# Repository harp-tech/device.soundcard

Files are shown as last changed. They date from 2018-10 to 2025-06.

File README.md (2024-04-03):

## Harp Soundcard
This is a high performance sound card with two output channels using 24 bits DACs at 192kHz sample rate. 

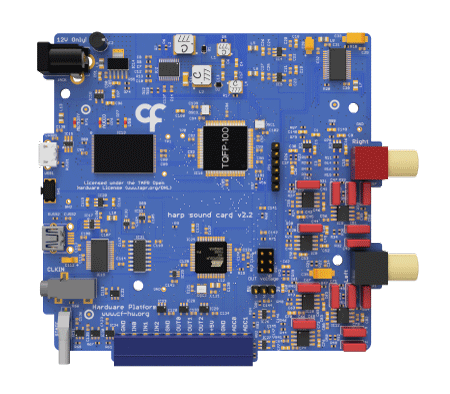
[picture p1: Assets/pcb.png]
HarpSoundcard


### Hardware Compatibility

| HW Version | Board                    | Board HW Version  | Notes                             |
| ---------- | ------------------------ |------------------ | --------------------------------- |
| **All**    | [Peripheral.AudioAmp][1] | >= 2.0            |                                   |

[1]: https://github.com/harp-tech/peripheral.audioamp

### Firmware Compatibility

| FW Version | Board                 | Board HW Version | Notes                                   |
| ---------- | --------------------- | ---------------- | --------------------------------------- |
| **>= 2.2** | [Device.SoundCard][2] | >= 1.0           | Bpod serial communication not supported |
| **<= 2.2** | [Device.SoundCard][2] | >= 1.0           |                                         |

[2]: https://github.com/harp-tech/device.soundcard

### Key Features ###

* Internal memory to store sounds, enabling low-latency sound delivery
* Pre-selected sounds can be triggered using an external TTL
* Internal wave generator allows the user to configure a pure tone without loading a sound file
* Stereo 24 bit @ 192 kHz maximum sampling rate outputs
* THD: -111dB (1 kHz @ 2 V rms)
* Noise Floor:	20 µV rms | -94 dB (20 Hz – 80 kHz)
* SNR:	100 dB | 113 dbA (20 Hz – 80 kHz @ 2 V rms)

### Connectivity ###

* 1x clock sync input (CLKIN) [stereo jack]
* 1x USB (for computer communication) [USB Mini-B]
* 1x micro USB (for sounds loading) [USB Micro-B]
* 1x 12V supply [barrel connector jack]
* 1x reset button [tactile switch]
* 1x output for the left channel [RCA]
* 1x output for the right channel [RCA]
* 3x general purpose digital outputs (3.3V or 5V) (OUT0-OUT2) [screw terminal]
* 3x general purpose digital inputs (5V tolerant) (IN0-IN2) [screw terminal]
* 2x analog inputs (3.3V máx - 5V tolerant) (ADC0-ADC1) [screw terminal]

## Interface ##

The interface with the Harp Soundcard can be done through [Bonsai](https://bonsai-rx.org/) or a dedicated GUI (Graphical User Interface).

### Install Graphical User Interface (GUI) ###

In order to use this GUI, there are some software that needs to be installed:

1 - Install the [drivers](https://bitbucket.org/fchampalimaud/downloads/downloads/UsbDriver-2.12.26.zip).

2 - Install the [runtime](https://bitbucket.org/fchampalimaud/downloads/downloads/Runtime-1.0.zip).

3 - Reboot the computer.

4 - Install the [GUI](https://bitbucket.org/fchampalimaud/downloads/downloads/Harp%20Sound%20Card%20v1.2.1.zip).

### Install Drivers ###

To install the proper drivers to interface with the device, follow the next steps in sequence.

1 - Connect both Harp Sound Card's USB ports to the computer.

2 - Launch the previously installed Harp Sound Card GUI.

3 - Click on the button Open Drivers folder and launch the zadig-2.3.exe.

4 - (1) Select the Harp Sound Card from the list. If the device is not available, go to Options -> List All Devices.

5 - (2) Select the WinUSB driver and click Install WCID Driver.

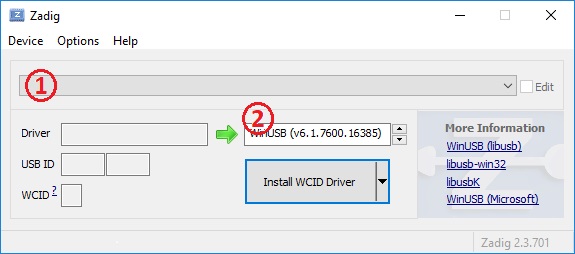
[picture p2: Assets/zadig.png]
Zadig


## Firmware ##

### Tagging Scheme ###

|Tag|Description|
|-|-|
|SoundCard-*|Firmware for the sound card's microcontroller (8 bits processor)|
|SoundCard.PIC32-*|Firmware for the sound card's 32 bits processor|

### Firmware Update ###

1 - Install the [Harp Converto to CSV](https://bitbucket.org/fchampalimaud/downloads/downloads/Harp_Convert_To_CSV_v1.8.3.zip).

2 - Open the Harp Convert to CSV application and write *bootloader* under List box on the Options tab

3 - Select the correspondent COM port and then select the firmware to be loaded for both microcontrollers 

# Licensing #

Each subdirectory will contain a license or, possibly, a set of licenses if it involves both hardware and software.

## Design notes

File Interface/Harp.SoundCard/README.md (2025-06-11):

## About

`Harp.SoundCard` provides an asynchronous API and reactive operators for data acquisition and control of [Harp SoundCard](https://harp-tech.org/api/Harp.SoundCard.html) devices.

## How to Use

To use `Harp.SoundCard` for visual reactive programming, please install this package using the [Bonsai package manager](https://bonsai-rx.org/docs/articles/packages.html).

The package can also be used from any .NET application:
```c#
using Harp.SoundCard;

using var device = await Device.CreateAsync("COM3");
var whoAmI = await device.ReadWhoAmIAsync();
var deviceName = await device.ReadDeviceNameAsync();
var timestamp = await device.ReadTimestampSecondsAsync();
Console.WriteLine($"{deviceName} WhoAmI: {whoAmI} Timestamp (s): {timestamp}");
```

## Additional Documentation

For additional documentation and examples, refer to the [official Harp documentation](https://harp-tech.org/api/Harp.SoundCard.html).

## Feedback & Contributing

`Harp.SoundCard` is released as open-source under the [MIT license](https://licenses.nuget.org/MIT). Bug reports and contributions are welcome at [the GitHub repository](https://github.com/harp-tech/device.soundcard).

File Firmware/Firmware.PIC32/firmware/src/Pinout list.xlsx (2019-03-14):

 | 0 | 1 | 2 | 3 | 4 | 5 | 6 | 7 | 8 | 9 | 10 | 11 | 12 | 13 | 14 | 15 |  | Pins | Description | Notes
RA | X | X | X | X | X | X | X | X |  | X | X |  |  |  | X | X |  | RB8 | !SS1
RB | X | X | X | X | X | X | X | X | X | X | X | X | X | X | X | X |  | RB9 | SDO1
RC |  | X | X | X | X |  |  |  |  |  |  |  | X | X | X | X |  | RB10 | SCK1
RD | X | X | X | X | X | X |  |  |  | X | X | X | X | X | X | X |  | RF0 | USB
RE | X | X | X | X | X | X | X | X | X | X |  |  |  |  |  |  |  | RF1 | AUDIO
RF | X | X | X | X | X | X |  |  | X |  |  |  | X | X |  |  |  | RG12 | TP0
RG | X | X |  |  |  |  | X | X | X | X |  |  | X | X | X | X |  | RG13 | TP1
 |  |  |  |  |  |  |  |  |  |  |  |  |  |  |  |  |  | RG14 | MEMORY
 |  |  |  |  |  |  |  |  |  |  |  |  |  |  |  |  |  | RD1 | EN_P12V
 |  |  |  |  |  |  |  |  |  |  |  |  |  |  |  |  |  | RD2 | EN_N12V
 |  |  |  |  |  |  |  |  |  |  |  |  |  |  |  |  |  | RB6-7 | ICE/ICD
 |  |  |  |  |  |  |  |  |  |  |  |  |  |  |  |  |  | RE0-7 | Memory | RE0 -> PMD0
 |  |  |  |  |  |  |  |  |  |  |  |  |  |  |  |  |  | RE8-9 | Don't use -- facilitates memory's access code
 |  |  |  |  |  |  |  |  |  |  |  |  |  |  |  |  |  | RC13 | REFCLKO1 (MCLK out) | I2S
 |  |  |  |  |  |  |  |  |  |  |  |  |  |  |  |  |  | RC14 | REFCLKI1 (OSC 24.576 MHz) (MCLK in) | I2S
 |  |  |  |  |  |  |  |  |  |  |  |  |  |  |  |  |  | RD9 | SS4 (out) (LRCLK) | I2S
 |  |  |  |  |  |  |  |  |  |  |  |  |  |  |  |  |  | RD10 | SCK4 (BCLK) | I2S
 |  |  |  |  |  |  |  |  |  |  |  |  |  |  |  |  |  | RD11 | SDO4 (SDATA) | I2S
 |  |  |  |  |  |  |  |  |  |  |  |  |  |  |  |  |  | RF2 | MUTE | Pin don't change
 |  |  |  |  |  |  |  |  |  |  |  |  |  |  |  |  |  | RF8 | ZEROR (not used)
 |  |  |  |  |  |  |  |  |  |  |  |  |  |  |  |  |  | RF3 | ZEROL (not used)
 |  |  |  |  |  |  |  |  |  |  |  |  |  |  |  |  |  | RF5 | DAC_RST | Pin don't change
 |  |  |  |  |  |  |  |  |  |  |  |  |  |  |  |  |  | RB12 (AN7) | ADC0_EZ
 |  |  |  |  |  |  |  |  |  |  |  |  |  |  |  |  |  | RB13 (AN8) | ADC1_EZ
 |  |  |  |  |  |  |  |  |  |  |  |  |  |  |  |  |  | RC3 | WE | Pin don't change
 |  |  |  |  |  |  |  |  |  |  |  |  |  |  |  |  |  | RC4 | RE | Pin don't change
 |  |  |  |  |  |  |  |  |  |  |  |  |  |  |  |  |  | RG7 | ALE | Pin don't change
 |  |  |  |  |  |  |  |  |  |  |  |  |  |  |  |  |  | RG8 | WP | Pin don't change
 |  |  |  |  |  |  |  |  |  |  |  |  |  |  |  |  |  | RG9 | BUSY | Pin don't change
 |  |  |  |  |  |  |  |  |  |  |  |  |  |  |  |  |  | RD12 | CE
 |  |  |  |  |  |  |  |  |  |  |  |  |  |  |  |  |  | RD13 | CLE
 |  |  |  |  |  |  |  |  |  |  |  |  |  |  |  |  | CMD_DATA | RA0-7 | PAR0-7: AVR <-> PIC32 Parallel bus with the Harp uController | (RA0 -> PAR0) Used to send configuration commands * | 2e-05
 |  |  |  |  |  |  |  |  |  |  |  |  |  |  |  |  |  | RA9-10, RA14-15 | Don't use -- facilitates parallel bus' code
 |  |  |  |  |  |  |  |  |  |  |  |  |  |  |  |  | CMD_WRITE | RB5 (INT3) | UC_IO0: AVR -> PIC32 | Command available on the PAR bus
 |  |  |  |  |  |  |  |  |  |  |  |  |  |  |  |  | CMD_LATCHED | RB4 | UC_IO1: AVR <- PIC32 | Command read from the PAR bus
 |  |  |  |  |  |  |  |  |  |  |  |  |  |  |  |  | SOUND_IS _ON | RG6 (INT2 if needed) | UC_IO2: AVR <- PIC32 | Command received has na error (must be set before CMD_LATCHED)
 |  |  |  |  |  |  |  |  |  |  |  |  |  |  |  |  | BOOTLOADER_EN | RB1 (INT4) | UC_IO3: AVR -> PIC32 | Enables bootloader on PIC32
 |  |  |  |  |  |  |  |  |  |  |  |  |  |  |  |  | CMD_NOT_EXEC | RB2 (INT1 if needed) | UC_IO4: AVR <- PIC32 | PIC32 has started (left bootloader or just boot)
 |  |  |  |  |  |  |  |  |  |  |  |  |  |  |  |  |  | RD0 (INT0) | IN0/TRIG: AVR & PIC32
 |  |  |  |  |  |  |  |  |  |  |  |  |  |  |  |  |  | IN01 | AVR
 |  |  |  |  |  |  |  |  |  |  |  |  |  |  |  |  |  | IN02 | AVR
 |  |  |  |  |  |  |  |  |  |  |  |  |  |  |  |  |  | RB3 | OUT00/SYNC: AVR & PIC32
 |  |  |  |  |  |  |  |  |  |  |  |  |  |  |  |  |  | OUT01 | AVR | 3.125e-08
 |  |  |  |  |  |  |  |  |  |  |  |  |  |  |  |  |  | OUT02 | AVR | 3.2e-05
 |  |  |  |  |  |  |  |  |  |  |  |  |  |  |  |  |  |  |  | 31250
 |  |  |  |  |  |  |  |  |  |  |  |  |  |  |  |  |  | RC2 (U2TX) | UART2_RX: AVR <- PIC32 (USED FOR PIC32 BOOLOADER) | Not used
 |  |  |  |  |  |  |  |  |  |  |  |  |  |  |  |  |  | RB0 (U2RX) | UART2_TX: AVR -> PIC32 (USED FOR PIC32 BOOLOADER) | Notifications
 |  |  |  |  |  |  |  |  |  |  |  |  |  |  |  |  | Plays a sound | 'P' n | d80
 |  |  |  |  |  |  |  |  |  |  |  |  |  |  |  |  | Stop all playback | 'X' | d88
 |  |  |  |  |  |  |  |  |  |  |  |  |  |  |  |  | Stop specific sound | x' n | d120

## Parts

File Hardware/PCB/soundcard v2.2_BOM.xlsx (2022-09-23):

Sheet: BOM
Part(s) | Quantity | Description | Distributor | Part. No.
IC1 | 1 | IC REG LINEAR 200MA TSOT23-5 | Digikey | ADP7118AUJZ-R7CT-ND
IC2 | 1 | IC REG BST SEPIC INV ADJ 20TSSOP | Mouser | 584-ADP5070AREZ
IC3 | 1 | IC REG LINEAR 200MA 5TSOT | Digikey | ADP7182AUJZ-R7CT-ND
IC4, IC5 | 2 | IC REG LINEAR 5V 150MA SOT23-5 | Digikey | LP2985A-50DBVT
IC6 | 1 | IC DAC AUDIO MULTIBIT 28-SSOP | Digikey | AD1955ARSZ-ND
IC7, IC8, IC9, IC10, IC11, IC12 | 6 | Amplificadores de precisão High Prec Low Noise Oper Amplifier | Mouser | 595-OPA228UA/2K5
IC13 | 1 | IC FLASH 2GBIT 48TSOP | Digikey | 1274-1040-ND‎
IC14 | 1 | Reguladores de tensão de LDO DMOS 1A LDO Reg | Mouser | 595-TPS73801DCQR
IC15, IC17 | 2 | TVS DIODE 5.25VWM 17VC SOT23-6 | Mouser | 511-USBLC6-2SC6
IC16 | 1 | IC MCU 32BIT 1MB FLASH 100TQFP | Mouser | 579-MZ1024EFM100IPF
IC19 | 1 | IC USB FS SERIAL UART 28-SSOP | Digikey | 768-1007-1-ND
IC18, IC20 | 2 | IC REG LINEAR 3.3V 250MA SOT23 | Digikey | 296-38557-1-ND
IC21 | 1 | DGTL ISO 3.75KV GEN PURP 16SOIC | Digikey | 336-2092-5-ND
IC22, IC24, IC30, IC31 | 4 | IC BUS BUFF TRI-ST N-INV SOT23-5 | Digikey | 296-11603-1-ND
IC23, IC28, IC29 | 3 | IC BUFF CMOS LVL/SFTR N-I 5TSOP | Digikey | M74VHC1GT50DTT1GOSCT-ND
IC25 | 1 | IC MCU 8BIT 128KB FLASH 44TQFP | Mouser | 556-ATXMEGA128A4U-AU
IC33, IC34 | 2 | IC BUFFER NON-INVERT 5.5V SC88A OE | Mouser | 863-M74VHC1GT126DF2G
IC35 | 1 | IC BUFFER NON-INVERT 5.5V SC88A !OE | Mouser | 863-M74VHC1GT125DF2G
R17 | 1 | RES SMD 5.36Ω 1% 0402 | Digikey | 541-5.36LLCT-ND
R5 | 1 | RES SMD 6.04Ω 1% 0402 | Digikey | 541-6.04LLCT-ND
R57 | 1 | RES SMD 1kΩ 1% 0402 | Digikey | P1.00KLCT-ND
R18, R75, R76, R77 | 4 | RES SMD 2.49kΩ 1% 0402 | Digikey | P2.49KLCT-ND
R10, R22 | 2 | RES SMD 2.8kΩ 1% 0402 | Digikey | P2.80KLCT-ND
R55, R80 | 2 | RES SMD 3.16kΩ 1% 0402 | Digikey | P3.16KLCT-ND
R7 | 1 | RES SMD 3.57kΩ 1% 0402 | Digikey | P3.57KLCT-ND
R13 | 1 | RES SMD 5.76kΩ 1% 0402 | Digikey | P5.76KLCT-ND
R8 | 1 | RES SMD 8.45kΩ 1% 0402 | Digikey | P8.45KLCT-ND
R74 | 1 | RES SMD 9.76kΩ 1% 0402 | Digikey | P9.76KLCT-ND
R3, R4, R15, R16, R56 | 5 | RES SMD 10kΩ 1% 0402 | Digikey | P10.0KLCT-ND
R12 | 1 | RES SMD 54.9kΩ 1% 0402 | Digikey | P54.9KLCT-ND
R6 | 1 | RES SMD 63.4kΩ 1% 0402 | Digikey | P63.4KLCT-ND
R9, R20, R61, R67, R68, R78, R79, R87, R88, R89 | 8 | RES SMD 100kΩ 5% 0402 | Digikey | P100KJCT-ND
R11 | 1 | RES SMD 150kΩ 1% 0402 | Digikey | P150KLCT-ND
R1, R2 | 2 | RES SMD 180kΩ 1% 0402 | Digikey | P180KLCT-ND
R14 | 1 | RES SMD 215kΩ 1% 0402 | Digikey | P215KLCT-ND
RUSB1, RUSB2 | 2 | RES SMD 1MΩ 5% 0402 | Digikey | P17211CT-ND
R27, R28, R37, R43, R44, R53, R66 | 7 | Resistores de Filme Fino - SMD 100Ω 0.5% 0402 25ppm | Mouser | 754-RG1005P-101DT10
R33, R34, R49, R50 | 4 | Resistores de Filme Fino - SMD 226Ω 0.1% 0402 25ppm | Mouser | 667-ERA-2AEB2260X
R35, R36, R51, R52 | 4 | Resistores de Filme Fino - SMD 324Ω 0.5% 0402 25ppm | Mouser | 754-RR0510P-3240D
R38, R54 | 2 | Resistores de Filme Fino - SMD 332Ω 0.5% 0402 25ppm | Mouser | 754-RG1005P-3320DT10
R31, R32, R47, R48 | 4 | Resistores de Filme Fino - SMD 681Ω 0.1% 0402 25ppm | Mouser | 667-ERA-2AEB6810X
R24, R25, R40, R41 | 4 | Resistores de Filme Fino - SMD 806Ω 0.5% 0402 25ppm | Mouser | 754-RG1005P-8060DT10
R23, R26, R29, R30, R39, R42, R45, R46 | 8 | Resistores de Filme Fino - SMD 2kΩ 0.1% 0402 25ppm | Mouser | 667-ERA-2AEB202X
R21 | 1 | Resistores de Filme Fino - SMD 2.21kΩ 0.5% 0402 25ppm | Mouser | 754-RR0510P-2211D
C8, C107, C108 | 3 | CAP SMD CER 47pF 50V ±5% C0G 0402 | Digikey | 490-8206-1-ND
C10 | 1 | CAP SMD CER 68pF 50V ±5% C0G 0402 | Digikey | 490-8219-1-ND‎
C38, C62 | 2 | CAP SMD CER 100pF 50V ±5% C0G 0603 | Digikey | 709-1147-1-ND
C7 | 1 | CAP SMD CER 820pF 50V ±5% C0G 0402 | Digikey | 445-8064-1-ND
CUSB1, CUSB2 | 2 | CAP SMD CER 4.7nF 50V ±10% X7R 0402 | Digikey | 490-4915-1-ND
C12 | 1 | CAP SMD CER 6.8nF 50V ±10% X7R 0402 | Digikey | 1276-1585-1-ND
C22, C23 | 2 | CAP SMD CER 10nF 50V ±10% X7R 0402 | Digikey | 490-4762-1-ND
C15, C20, C21, C24, C25, C29, C30, C31, C32, C84, C88, C89, C90, C92, C93, C94, C95, C96, C97, C98, C99, C101, C102, C104, C105, C106, C111, C113, C114, C117, C118, C119, C120, C121, C123, C126, C127, C128, C133, C134, C135, C136, C138, C139, C143 | 45 | CAP SMD CER 100nF 25V ±10% X5R 0402 | Digikey | 1276-1043-1-ND
C34, C37, C39, C40, C41, C42, C49, C50, C55, C56, C61, C63, C64, C65, C66, C73, C74, C79, C80 | 19 | CAP SMD CER 100nF 25V ±10% X5R 0402 | Digikey | 1276-1043-1-ND
C130, C131 | 2 | CAP SMD CER 330nF 10V ±10% X5R 0402 | Digikey | 1276-6665-1-ND
C3, C14, C137 | 3 | CAP SMD CER 1uF 25V ±10% X5R 0402 | Digikey | 1276-1445-1-ND
C4, C6, C13, C17, C148, C149 | 6 | CAP SMD CER 1uF 25V ±10% X5R 0603 | Digikey | 490-16608-1-ND
C1, C5, C9, C16 | 4 | CAP SMD CER 2.2uF 35V ±10% X5R 0603 | Digikey | 445-8025-1-ND
C112 | 1 | CAP SMD TAN 4.7uF 6.3V ±10% 1206 | Digikey | 399-9717-1-ND
C11 | 1 | CAP SMD CER 10uF 25V ±20% X5R 1206 | Digikey | 445-8806-1-ND
C18, C19, C26, C27, C85, C86, C87, C91, C100, C115, C116, C132 | 12 | CAP SMD CER 10uF 25V ±20% X5R 0603 | Digikey | 445-9015-1-ND
C28 | 1 | CAP SMD TAN 10uF 16V ±20% 1411 | Digikey | 399-8446-1-ND
C33, C35 | 2 | CAP SMD TAN 47uF 16V ±10% 2312 | Digikey | 399-9763-1-ND
C43, C44, C67, C68 | 4 | CAP TH FILM 100pF 100V ±5% PP Radial | Mouser | 505-FKP2100/100/5
C51, C54, C75, C78 | 4 | CAP TH FILM 2.7nF 100V ±2.5% PP Radial | Mouser | 505-FKP2D012701DHA00
C57, C81 | 2 | CAP TH FILM 3.9nF 63V ±5% PP Radial | Mouser | 505-FKP2-3900632.5A
C47, C48, C71, C72 | 4 | CAP TH FILM 5.6nF 63V ±5% PP Radial | Mouser | 505-FKP2C015601DHC00
C36, C45, C46, C52, C53, C58, C59, C60, C69, C70, C76, C77, C82, C83 | 14 | CAP SMD CER 4.7uF 25V ±20% X5R 0603 | Mouser | 81-GRM188R61E475ME1J
C2 | 1 | CAP TH ELEC 68uF 25V ±20% Alum Radial | Digikey | P14412-ND
L1, L4 | 2 | IND SMD 1.5uH 2.2A ±20% | Mouser | 994-LPS4012-152MRB
L2 | 1 | IND SMD 3.3uH 1.35A ±20% | Mouser | 994-LPS6225-332MRB
L3 | 1 | IND SMD 15uH 1.2A ±20% | Mouser | 994-LPS6225-153MRB
L5, L6, L7, L8, L9 | 5 | FERRITE BEAD 600Ω 500mA 300mΩ 0805 | Digikey | 240-2399-1-ND
L10, L12, L13 | 3 | FERRITE BEAD 70Ω 1.5A 50mΩ 0805 | Digikey | 240-2389-1-ND
D1, D2 | 2 | DIODE SCHOTTKY 30V 1A SOD323 | Digikey | BAS3010A03WE6327HTSA1CT-ND
STATE | 1 | LED GREEN 0603 SMD | Digikey | 751-1176-1-ND
MEMORY, AUDIO, USB | 3 | LED RED 0603 SMD | Digikey | 751-1182-1-ND
OSC1 | 1 | OSC MEMS 24.000MHZ CMOS | Mouser | ASEM1-24.000MHZ-LC-T
OSC2 | 1 | OSC MEMS 32.0000MHZ CMOS | Mouser | 579-SC1001CI50320000
OSC3 | 1 | OSC MEMS 24.576MHZ CMOS | Digikey | ASEMB-24.576MHZ-LY-T
USB2 | 1 | RECEPT MINI USB2.0 5POS | Digikey | H2960CT-ND
USB1 | 1 | CONN RCPT USB MICRO B SMD | Mouser | 798-ZX62D-B-5P830
CLKIN | 1 | JACK STEREO 3.5MM SMD R/A | Digikey | SC1489-1-ND
JP2 | 1 | CONN HEADER 3POS .100 STR | Digikey | 609-3470-ND
 | 1 | CONN JUMPER SHORTING GOLD FLASH | Digikey | S9001-ND
JP1 | 1 | CONN HEADER 6POS .100 STR | Digikey | 609-3256-ND
PDI | 1 | CONN HEADER 6POS .100 STR | Digikey | 609-3210-ND
J3 | 1 | CONN RCA JACK MONO 3.2MM R/A RED | Digikey | SC1853-ND
J4 | 1 | CONN RCA JACK MONO 3.2MM R/A BLACK | Digikey | SC1852-ND
JACK | 1 | CC PCB 2.1MM | Mouser | 163-179PH-EX
SW1 | 1 | SWITCH TACTILE SPST-NO 0.05A 50V | Digikey | 401-1097-1-ND
 | 1 | IMO 20.1550M/10-E Pluggable Terminal Block, 3.5 mm, 10 Ways | Farnell | 2575213
X1 | 1 | IMO 20.155MH/10-E Terminal Block, Header, 3.5 mm, 10 Ways | Farnell | 2575221
USB Cable Mini | 1 | USB A - MINI-B 1.5M - MINI-B 1.5M BLACK | Mouser | 538-88732-8702
USB Cable Micro | 1 | Cabo USB 2.0A to Micro B Cable 1M Blk Nylon | Mouser | 734-ES-UB1-100-BK
 | 3 | LIGHT PIPE ROUND 4MM CLEAR | Digikey | LPC_096_CTP-ND
 | 1 | Tubos de Luz LED CML LIGHTPIPE | Mouser | 606-7513D2-L
 | 1 | AC/DC Power Supply, Class II, 1 Output, 12 W, 12 V, 1 A | Farnell | 2524421
 | 1 | Heat Sink, Square, For PGA's, 18.6 °C/W, PGA, 14 mm, 14 mm, 14 mm | Farnell | 1850037
Components | 281
Licensed under the TAPR Open Hardware License (www.tapr.org/OHL)
Copyright 2021 Artur Silva, Filipe Carvalho

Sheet: Sheet1
r1 | 95300
r2 | 13300
11.46493395
5.273333333

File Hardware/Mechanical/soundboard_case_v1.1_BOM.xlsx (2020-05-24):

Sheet: BOM
Board | Part(s) | Quantity | Description | Distributor | Part. No. | Price/Unit | Total Price
 |  | 4 | Screw, Flat / Countersunk Head Pozidriv, M3, Nylon, 10 mm Length | Farnell | 1514427 | €0.14 | €0.55
 |  | 4 | Bumper / Feet, Recessed, Screw, Rubber, 6.4 mm, Round, Black | Farnell | 1651664 | €0.12 | €0.50
 |  | 4 | Standoff, Nylon 6.6 (Polyamide 6.6), M3, Hex Male-Female, 11 mm | Farnell | 2988203 | €0.91 | €3.64
 |  | 4 | Nut, Hex, M3, Nylon 6.6 | Farnell | 2472687 | €0.05 | €0.20
 | Components | 16 |  |  |  |  | €4.89
 | PCB
 | Assembly
 |  |  |  |  |  | Total | €4.89
 | Licensed under the TAPR Open Hardware License (www.tapr.org/OHL)
 | Copyright 2017-2019 Artur Silva, Dario Bento, Paulo Carriço and Filipe Carvalho

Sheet: Sheet1
r1 | 95300
r2 | 13300
11.46493395
5.273333333

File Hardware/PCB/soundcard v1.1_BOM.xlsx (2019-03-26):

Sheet: BOM
Board | Part(s) | Quantity | Description | Distributor | Part. No.
 | IC1 | 1 | IC REG LINEAR 200MA TSOT23-5 | Digikey | ADP7118AUJZ-R7CT-ND
 | IC2 | 1 | IC REG BST SEPIC INV ADJ 20TSSOP | Digikey | ADP5070AREZ-R7CT-ND
 | IC3 | 1 | IC REG LINEAR 200MA 5TSOT | Digikey | ADP7182AUJZ-R7CT-ND
 | IC4, IC5 | 2 | IC REG LINEAR 5V 200MA 8SOIC | Digikey | ADP3303ARZ-5-ND
 | IC6 | 1 | IC DAC AUDIO MULTIBIT 28-SSOP | Digikey | AD1955ARSZ-ND
 | IC7, IC8, IC9, IC10, IC11, IC12 | 6 | IC OPAMP GP 110MHZ 8SOIC | Digikey | AD797BRZ-ND
 | IC13 | 1 | IC FLASH 2GBIT 48TSOP | Digikey | 1274-1040-ND‎
 | IC14, IC32 | 2 | IC REG LIN POS ADJ 1A SOT223-6 | Digikey | 296-39489-1-ND
 | IC15, IC17 | 2 | TVS DIODE 5.25VWM 17VC SOT23-6 | Digikey | 497-5235-1-ND
 | IC16 | 1 | IC MCU 32BIT 2MB FLASH 100TQFP | Digikey | PIC32MZ2048EFM100-I/PF
 | IC19 | 1 | IC USB FS SERIAL UART 28-SSOP | Digikey | 768-1007-1-ND
 | IC18, IC20 | 2 | IC REG LINEAR 3.3V 250MA SOT23 | Digikey | 296-38557-1-ND
 | IC21 | 1 | DGTL ISO 3.75KV GEN PURP 16SOIC | Digikey | 336-2092-5-ND
 | IC22, IC24, IC30, IC31 | 4 | IC BUS BUFF TRI-ST N-INV SOT23-5 | Digikey | 296-11603-1-ND
 | IC23, IC28, IC29 | 3 | IC BUFF CMOS LVL/SFTR N-I 5TSOP | Digikey | M74VHC1GT50DTT1GOSCT-ND
 | IC25 | 1 | IC MCU 8BIT 128KB FLASH 44TQFP | Digikey | ATXMEGA128A4U-AU-ND
 | IC26 | 1 | DGTL ISO 2.5KV GEN PURP 16SOIC | Digikey | 336-2568-ND
 | IC27 | 1 | IC DVR/RCVR RS-485 3.3V 8-SOIC | Digikey | 296-19626-1-ND
 | IC33, IC34 | 2 | IC BUFFER NON-INVERT 5.5V SC88A OE | Digikey | M74VHC1GT126DF2GOSCT-ND
 | IC35 | 1 | IC BUFFER NON-INVERT 5.5V SC88A !OE | Digikey | M74VHC1GT125DF2GOSCT-ND
 | IC37, IC38 | 2 | Amplificadores operacionais - Amp Op 2.2V 50MHz Low Noise Single Supply | Mouser | 595-OPA365AIDBVR
 | R17 | 1 | RES SMD 5.36Ω 1% 0402 | Digikey | 541-5.36LLCT-ND
 | R5 | 1 | RES SMD 6.04Ω 1% 0402 | Digikey | 541-6.04LLCT-ND
 | R69, R70 | 2 | RES SMD 33Ω 1% 0402 | Digikey | P33.0LCT-ND
 | R66 | 1 | RES SMD 68Ω 1% 0402 | Digikey | P68.0LCT-ND
 | R57, R63 | 2 | RES SMD 1kΩ 1% 0402 | Digikey | P1.00KLCT-ND
 | R10 | 1 | RES SMD 2.8kΩ 1% 0402 | Digikey | P2.80KLCT-ND
 | R75, R76, R77 | 3 | RES SMD 2.05kΩ 1% 0402 | Digikey | P2.05KLCT-ND
 | R19, R55, R60, R62, R71, R72, R80 | 7 | RES SMD 3.16kΩ 1% 0402 | Digikey | P3.16KLCT-ND
 | R7 | 1 | RES SMD 3.57kΩ 1% 0402 | Digikey | P3.57KLCT-ND
 | R13 | 1 | RES SMD 5.76kΩ 1% 0402 | Digikey | P5.76KLCT-ND
 | R8 | 1 | RES SMD 8.45kΩ 1% 0402 | Digikey | P8.45KLCT-ND
 | R73, R74 | 2 | RES SMD 9.76kΩ 1% 0402 | Digikey | P9.76KLCT-ND
 | R3, R4, R15, R16, R56, R81, R82 | 7 | RES SMD 10kΩ 1% 0402 | Digikey | P10.0KLCT-ND
 | R84, R86 | 2 | RES SMD 16kΩ 1% 0402 | Digikey | P16.0KLCT-ND
 | R83, R85 | 2 | RES SMD 24kΩ 1% 0402 | Digikey | P24.0KLCT-ND
 | R12 | 1 | RES SMD 54.9kΩ 1% 0402 | Digikey | P54.9KLCT-ND
 | R6 | 1 | RES SMD 63.4kΩ 1% 0402 | Digikey | P63.4KLCT-ND
 | R9, R20, R61, R67, R68, R78, R79, R87, R88, R89 | 8 | RES SMD 100kΩ 5% 0402 | Digikey | P100KJCT-ND
 | R11 | 1 | RES SMD 150kΩ 1% 0402 | Digikey | P150KLCT-ND
 | R1, R2 | 2 | RES SMD 180kΩ 1% 0402 | Digikey | P180KLCT-ND
 | R14 | 1 | RES SMD 215kΩ 1% 0402 | Digikey | P215KLCT-ND
 | RUSB1, RUSB2 | 2 | RES SMD 1MΩ 5% 0402 | Digikey | P17211CT-ND
 | R27, R28, R37, R43, R44, R53 | 6 | RES TH 100Ω 1% Axial | Digikey | 100XBK-ND
 | R33, R34, R49, R50 | 4 | RES TH 226Ω 0.1% Axial | Mouser | 66-RC55LF-D-226
 | R35, R36, R51, R52 | 4 | RES TH 324Ω 1% Axial | Digikey | 324XBK-ND
 | R38, R54 | 2 | RES TH 332Ω 1% Axial | Digikey | 332XBK-ND
 | R31, R32, R47, R48 | 4 | RES TH 681Ω 0.1% Axial | Mouser | 66-RC55LF-D-681
 | R24, R25, R40, R41 | 4 | RES TH 806Ω 1% Axial | Digikey | 806XBK-ND
 | R23, R26, R29, R30, R39, R42, R45, R46 | 8 | RES TH 2kΩ 0.1% Axial | Mouser | 756-RC55Y-2K0BI
 | R21 | 1 | RES TH 2.21kΩ 1% Axial | Mouser | 2.21KXBK-ND
 | R18 | 1 | RES TH 2.49kΩ 1% Axial | Digikey | 2.49KXBK-ND
 | R22 | 1 | RES TH 2.80kΩ 1% Axial | Digikey | 2.80KXBK-ND
 | C8, C107, C108 | 3 | CAP SMD CER 47pF 50V ±5% C0G 0402 | Digikey | 490-8206-1-ND
 | C10 | 1 | CAP SMD CER 68pF 50V ±5% C0G 0402 | Digikey | 490-8219-1-ND‎
 | C38, C62 | 2 | CAP SMD CER 100pF 50V ±5% C0G 0603 | Digikey | 709-1147-1-ND
 | C7 | 1 | CAP SMD CER 820pF 50V ±5% C0G 0402 | Digikey | 445-8064-1-ND
 | CUSB1, CUSB2 | 2 | CAP SMD CER 4.7nF 50V ±10% X7R 0402 | Digikey | 490-4915-1-ND
 | C12 | 1 | CAP SMD CER 6.8nF 50V ±10% X7R 0402 | Digikey | 1276-1585-1-ND
 | C22, C23 | 2 | CAP SMD CER 10nF 50V ±10% X7R 0402 | Digikey | 490-4762-1-ND
 | C144, C145 | 2 | CAP SMD CER 15nF 16V ±10% X7R 0402 | Digikey | 1276-1524-1-ND
 | C15, C20, C21, C24, C25, C29, C30, C31, C32, C84, C88, C89, C90, C92, C93, C94, C95, C96, C97, C98, C99, C101, C102, C104, C105, C106, C109, C111, C113, C114, C117, C118, C119, C120, C121, C122, C123, C124, C125, C126, C127, C128, C129, C133, C134, C135, C136, C138, C139, C140, C141, C142, C143, C146, C147 | 55 | CAP SMD CER 100nF 25V ±10% X5R 0402 | Digikey | 1276-1043-1-ND
 | C130, C131 | 2 | CAP SMD CER 330nF 10V ±10% X5R 0402 | Digikey | 1276-6665-1-ND
 | C3, C14, C137 | 3 | CAP SMD CER 1uF 25V ±10% X5R 0402 | Digikey | 1276-1445-1-ND
 | C4, C6, C13, C17, C148, C149 | 6 | CAP SMD CER 1uF 25V ±10% X5R 0603 | Digikey | 490-16608-1-ND
 | C1, C5, C9, C16 | 4 | CAP SMD CER 2.2uF 35V ±10% X5R 0603 | Digikey | 445-8025-1-ND
 | C112 | 1 | CAP SMD TAN 4.7uF 6.3V ±10% 1206 | Digikey | 399-9717-1-ND
 | C11 | 1 | CAP SMD CER 10uF 25V ±20% X5R 1206 | Digikey | 445-8806-1-ND
 | C18, C19, C26, C27, C85, C86, C87, C91, C100, C103, C110, C115, C116, C132 | 14 | CAP SMD CER 10uF 25V ±20% X5R 0603 | Digikey | 445-9015-1-ND
 | C28 | 1 | CAP SMD TAN 10uF 16V ±20% 1411 | Digikey | 399-8446-1-ND
 | C33 | 1 | CAP SMD TAN 47uF 16V ±10% 2312 | Digikey | 399-9763-1-ND
 | C43, C44, C67, C68 | 4 | CAP TH FILM 100pF 100V ±5% PP Radial | Mouser | 505-FKP2100/100/5
 | C51, C54, C75, C78 | 4 | CAP TH FILM 2.7nF 100V ±2.5% PP Radial | Mouser | 505-FKP2D012701DHA00
 | C57, C81 | 2 | CAP TH FILM 3.9nF 63V ±5% PP Radial | Mouser | 505-FKP2-3900632.5A
 | C47, C48, C71, C72 | 4 | CAP TH FILM 5.6nF 63V ±5% PP Radial | Mouser | 505-FKP2C015601DHC00
 | C34, C37, C39, C40, C41, C42, C49, C50, C55, C56, C61, C63, C64, C65, C66, C73, C74, C79, C80 | 19 | CAP TH FILM 100nF 100V ±5% Poly Radial | Mouser | BFC237022104
 | C36, C45, C46, C52, C53, C58, C59, C60, C69, C70, C76, C77, C82, C83 | 14 | CAP TH ELEC 4.7uF 35V ±20% Alum Radial | Digikey | 493-1847-ND
 | C35 | 1 | CAP TH ELEC 47uF 16V ±20% Alum Radial | Digikey | P11196-ND
 | C2 | 1 | CAP TH ELEC 68uF 25V ±20% Alum Radial | Digikey | P14412-ND
 | L1, L4 | 2 | IND SMD 1.5uH 2.2A ±20% | Mouser | 994-LPS4012-152MRB
 | L2 | 1 | IND SMD 3.3uH 1.35A ±20% | Mouser | 994-LPS6225-332MRB
 | L3 | 1 | IND SMD 15uH 1.2A ±20% | Mouser | 994-LPS6225-153MRB
 | L5, L6, L7, L8, L9, L11 | 6 | FERRITE BEAD 600Ω 500mA 300mΩ 0805 | Digikey | 240-2399-1-ND
 | L12 | 1 | FERRITE BEAD 330Ω 1.5A 70mΩ 0603 | Digikey | 490-3997-1-ND
 | L10, L13 | 2 | FERRITE BEAD 70Ω 1.5A 50mΩ 0805 | Digikey | 240-2389-1-ND
 | D1, D2 | 2 | DIODE SCHOTTKY 30V 1A SOD323 | Digikey | BAS3010A03WE6327HTSA1CT-ND
 | STATE | 1 | LED GREEN 0603 SMD | Digikey | 751-1176-1-ND
 | MEMORY, AUDIO, USB | 3 | LED RED 0603 SMD | Digikey | 751-1182-1-ND
 | OSC1 | 1 | OSC MEMS 24.000MHZ CMOS | Digikey | 535-11728-1-ND
 | OSC2 | 1 | OSC MEMS 32.0000MHZ CMOS | Digikey | DSC1001CI5-032.0000-ND
 | OSC3 | 1 | OSC MEMS 24.576MHZ CMOS | Digikey | 535-11156-1-ND
 | USB2 | 1 | RECEPT MINI USB2.0 5POS | Digikey | H2960CT-ND
 | USB1 | 1 | CONN RCPT USB MICRO B SMD | Digikey | H125272CT-ND
 | CLKIN | 1 | JACK STEREO 3.5MM SMD R/A | Digikey | SC1489-1-ND
 | JP2 | 1 | CONN HEADER 3POS .100 STR | Digikey | 609-3470-ND
 | JP1 | 1 | CONN HEADER 6POS .100 STR | Digikey | 609-3256-ND
 | PDI | 1 | CONN HEADER 6POS .100 STR | Digikey | 609-3210-ND
 | IN, OUT | 2 | CONN BNC JACK R/A 50 OHM | Digikey | A32244-ND
 | J1, J2 | 2 | CONN MOD JACK 8P8C R/A UNSHLD | Digikey | A105009CT-ND
 | J3 | 1 | CONN RCA JACK MONO 3.2MM R/A RED | Digikey | SC1853-ND
 | J4 | 1 | CONN RCA JACK MONO 3.2MM R/A BLACK | Digikey | SC1852-ND
 | JACK | 1 | CC PCB 2.1MM | Mouser | 163-179PH-EX
 | SW1 | 1 | SWITCH TACTILE SPST-NO 0.05A 50V | Digikey | 401-1097-1-ND | 105 | Number of Unique Parts (the number of BOM line items)
 |  | 4 | RFI SHIELD CLIP MINI TIN SMD | Digikey | 952-2517-1-ND | 216 | Number of SMT Parts
 | X1 | 1 | IMO 20.155MH/10-E Terminal Block, Header, 3.5 mm, 10 Ways | Farnell | 2575221 | 98 | Number of Through-Hole Parts
 | EMI | 1 | RFI SHIELD CAN 30X30X5MM | Digikey | 952-2641-ND
 |  | 1 | IMO 20.1550M/10-E Pluggable Terminal Block, 3.5 mm, 10 Ways | Farnell | 2575213
 |  | 1 | CONN JUMPER SHORTING GOLD FLASH | Digikey | S9001-ND
 | USB Cable Mini | 1 | USB A - MINI-B 1.5M - MINI-B 1.5M BLACK | Mouser | 538-88732-8702
 | USB Cable Micro | 1 | Cabo USB 2.0A to Micro B Cable 1M Blk Nylon | Mouser | 734-ES-UB1-100-BK
 |  | 3 | LIGHT PIPE ROUND 4MM CLEAR | Digikey | LPC_096_CTP-ND
 |  | 3 | LIGHTPIPE GROMMET 4MM | Digikey | RTN_150-ND
 |  | 1 | Tubos de Luz LED CML LIGHTPIPE | Mouser | 606-7513D2-L
 |  | 1 | AC/DC Power Supply, Class II, 1 Output, 12 W, 12 V, 1 A | Farnell | 2524421
 |  | 2 | Heat Sink, Square, For PGA's, 18.6 °C/W, PGA, 14 mm, 14 mm, 14 mm | Farnell | 1850037
 |  | 4 | Socket Screw, Cap, Hex Socket, Steel, 6 mm, M4, Pack of 100 | Farnell | 1419609
 |  | 4 | Bumper / Feet, Recess, Pack 100, Screw, Rubber, 12.7 mm, Round, Black | Farnell | 2527424
 |  | 4 | Machine Screw, M4, 12 mm, Nylon 6.6, Flat / Countersunk Head Slotted | Farnell | 7071073
 |  | 8 | Nut, Hex, M3, Nylon 6.6 | Farnell | 2472687
 |  | 4 | Machine Screw, M3, 10 mm, Nylon (Polyamide), Pan Head Slotted | Farnell | 1514410
 | Components | 353
 | Licensed under the TAPR Open Hardware License (www.tapr.org/OHL)
 | Copyright 2017-2019 Artur Silva, Dario Bento, Paulo Carriço and Filipe Carvalho

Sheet: Sheet1
r1 | 95300
r2 | 13300
11.46493395
5.273333333

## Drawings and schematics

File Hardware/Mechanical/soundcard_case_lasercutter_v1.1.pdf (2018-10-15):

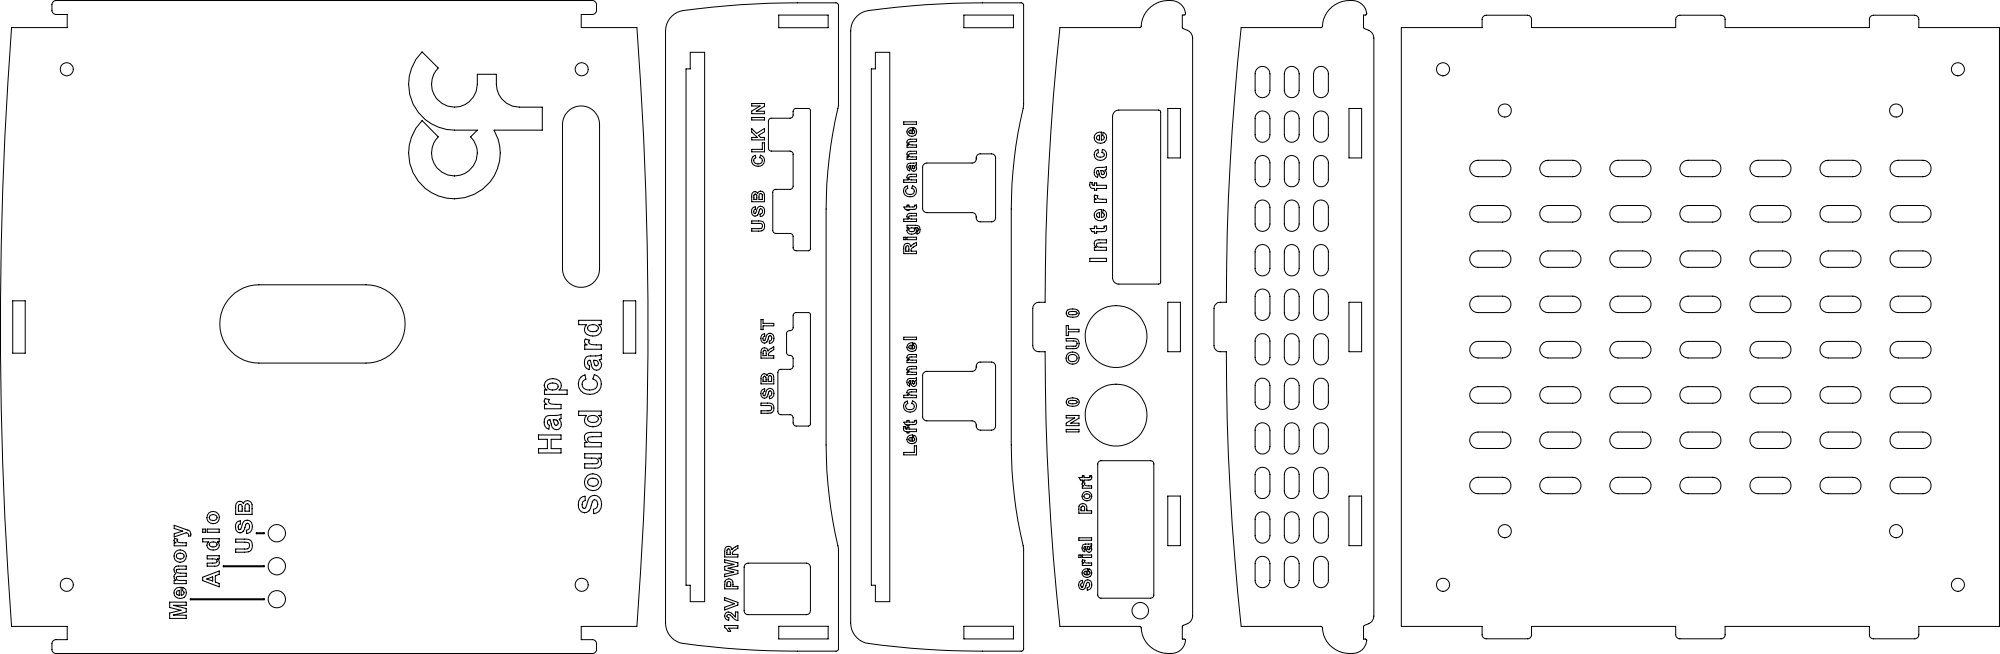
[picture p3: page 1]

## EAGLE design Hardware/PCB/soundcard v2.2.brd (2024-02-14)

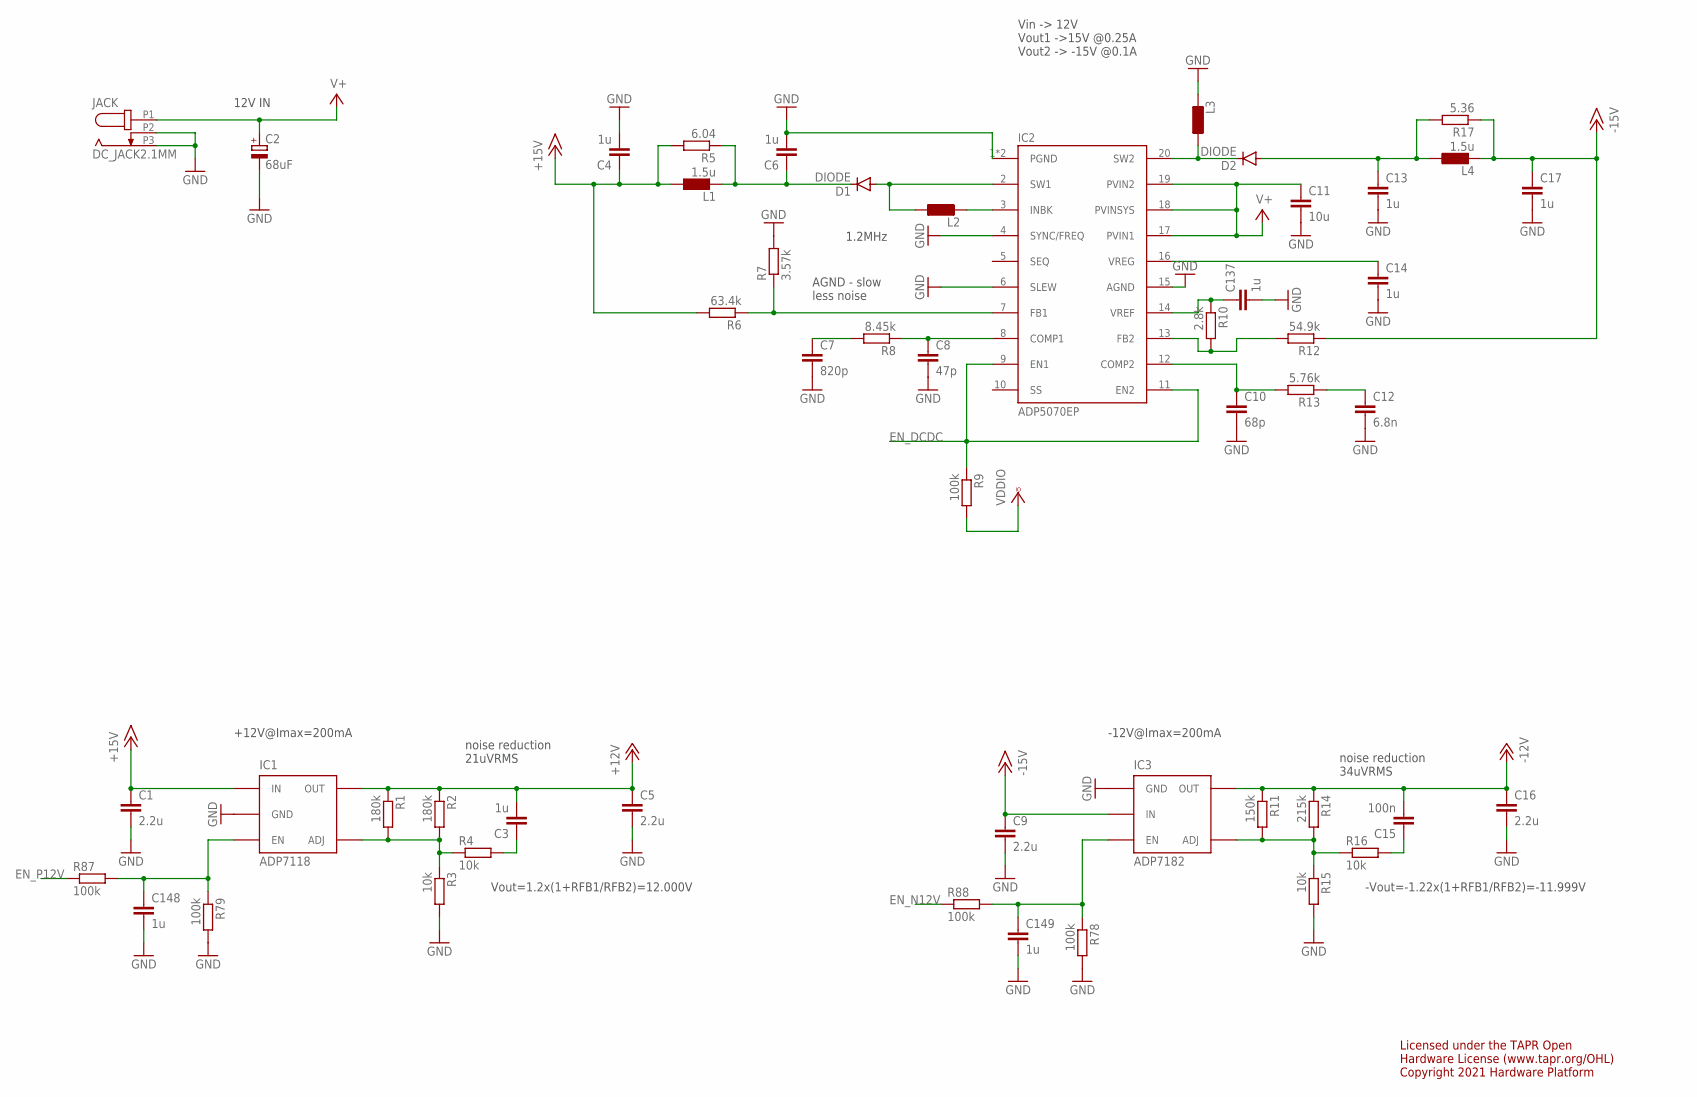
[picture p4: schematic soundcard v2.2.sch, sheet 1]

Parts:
C1, C5, C9, C16: 2.2u; C0603
C2: 68uF; E2-5
C3, C14, C137: 1u; C0402
C4, C6, C13, C17, C148, C149: 1u; C0603
C7: 820p; C0402
C8: 47p; C0402
C10: 68p; C0402
C11: 10u; C1206
C12: 6.8n; C0402
C15: 100n; C0402
D1, D2: DIODE; SOD-323-DIODE
IC1: ADP7118; TSOT23-5
IC2: ADP5070EP; TSSOP-EP-20
IC3: ADP7182; TSOT23-5
JACK: DC_JACK2.1MM; DC_POWER_INPUT_2.1MM
L1, L4: 1.5u; IND_LPS4012_V2
L2, L3: INDLPS6225_L; IND_LPS6225_V2
R1, R2: 180k; R0402
R3, R4, R15, R16: 10k; R0402
R5: 6.04; R0402
R6: 63.4k; R0402
R7: 3.57k; R0402
R8: 8.45k; R0402
R9, R78, R79, R87, R88: 100k; R0402
R10: 2.8k; R0402
R11: 150k; R0402
R12: 54.9k; R0402
R13: 5.76k; R0402
R14: 215k; R0402
R17: 5.36; R0402

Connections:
+12V: C3.2, C5.1, IC1.5 (OUT), R1.1, R2.1; also elsewhere on the board
+15V: C1.1, C4.1, IC1.1 (IN), L1.1, R5.2, R6.2
-12V: C15.2, C16.1, IC3.5 (OUT), R11.1, R14.1; also elsewhere on the board
-15V: C9.1, C17.1, IC3.2 (IN), L4.2, R12.1, R17.1
EN_DCDC: IC2.9 (EN1), IC2.11 (EN2), R9.1; also elsewhere on the board
EN_N12V: R88.1; also elsewhere on the board
EN_P12V: R87.1; also elsewhere on the board
GND: C1.2, C2.-, C4.2, C5.2, C6.2, C7.2, C8.2, C9.2, C10.2, C11.2, C12.2, C13.2, C14.2, C16.2, C17.2, C137.2, C148.2, C149.2, IC1.2 (GND), IC2.1 (PGND), IC2.4 (SYNC/FREQ), IC2.6 (SLEW), IC2.15 (AGND), IC2.EPAD (PGND), IC3.1 (GND), JACK.P2 (2), JACK.P3 (3), L3.2, R3.2, R7.2, R15.2, R78.2, R79.2; also elsewhere on the board
INBK: IC2.3 (INBK), L2.2
unnamed: IC2.7 (FB1), R6.1, R7.1
unnamed: C7.1, R8.2
unnamed: C8.1, IC2.8 (COMP1), R8.1
unnamed: C10.1, IC2.12 (COMP2), R13.2
unnamed: C12.1, R13.1
unnamed: C14.1, IC2.16 (VREG)
unnamed: C3.1, R4.2
unnamed: IC2.13 (FB2), R10.2, R12.2
unnamed: C137.1, IC2.14 (VREF), R10.1
unnamed: IC1.4 (ADJ), R1.2, R2.2, R3.1, R4.1
unnamed: IC3.4 (ADJ), R11.2, R14.2, R15.1, R16.1
unnamed: C15.1, R16.2
unnamed: C148.1, IC1.3 (EN), R79.1, R87.2
unnamed: C149.1, IC3.3 (EN), R78.1, R88.2
OUTN15: C13.1, D2.A, L4.1, R17.2
OUTP15: C6.1, D1.C, L1.2, R5.1
OUT_SW1: D1.A, IC2.2 (SW1), L2.1
OUT_SW2: D2.C, IC2.20 (SW2), L3.1
V+: C2.+, C11.1, IC2.17 (PVIN1), IC2.18 (PVINSYS), IC2.19 (PVIN2), JACK.P1 (1); also elsewhere on the board
VCCIO: R9.2; also elsewhere on the board

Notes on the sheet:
Vin -> 12V Vout1 ->15V @0.25A Vout2 -> -15V @0.1A
1.2MHz
AGND - slow less noise
noise reduction 34uVRMS
-12V@Imax=200mA
-Vout=-1.22x(1+RFB1/RFB2)=-11.999V
+12V@Imax=200mA
Vout=1.2x(1+RFB1/RFB2)=12.000V
noise reduction 21uVRMS
Licensed under the TAPR Open Hardware License (www.tapr.org/OHL) Copyright 2021 Hardware Platform
12V IN

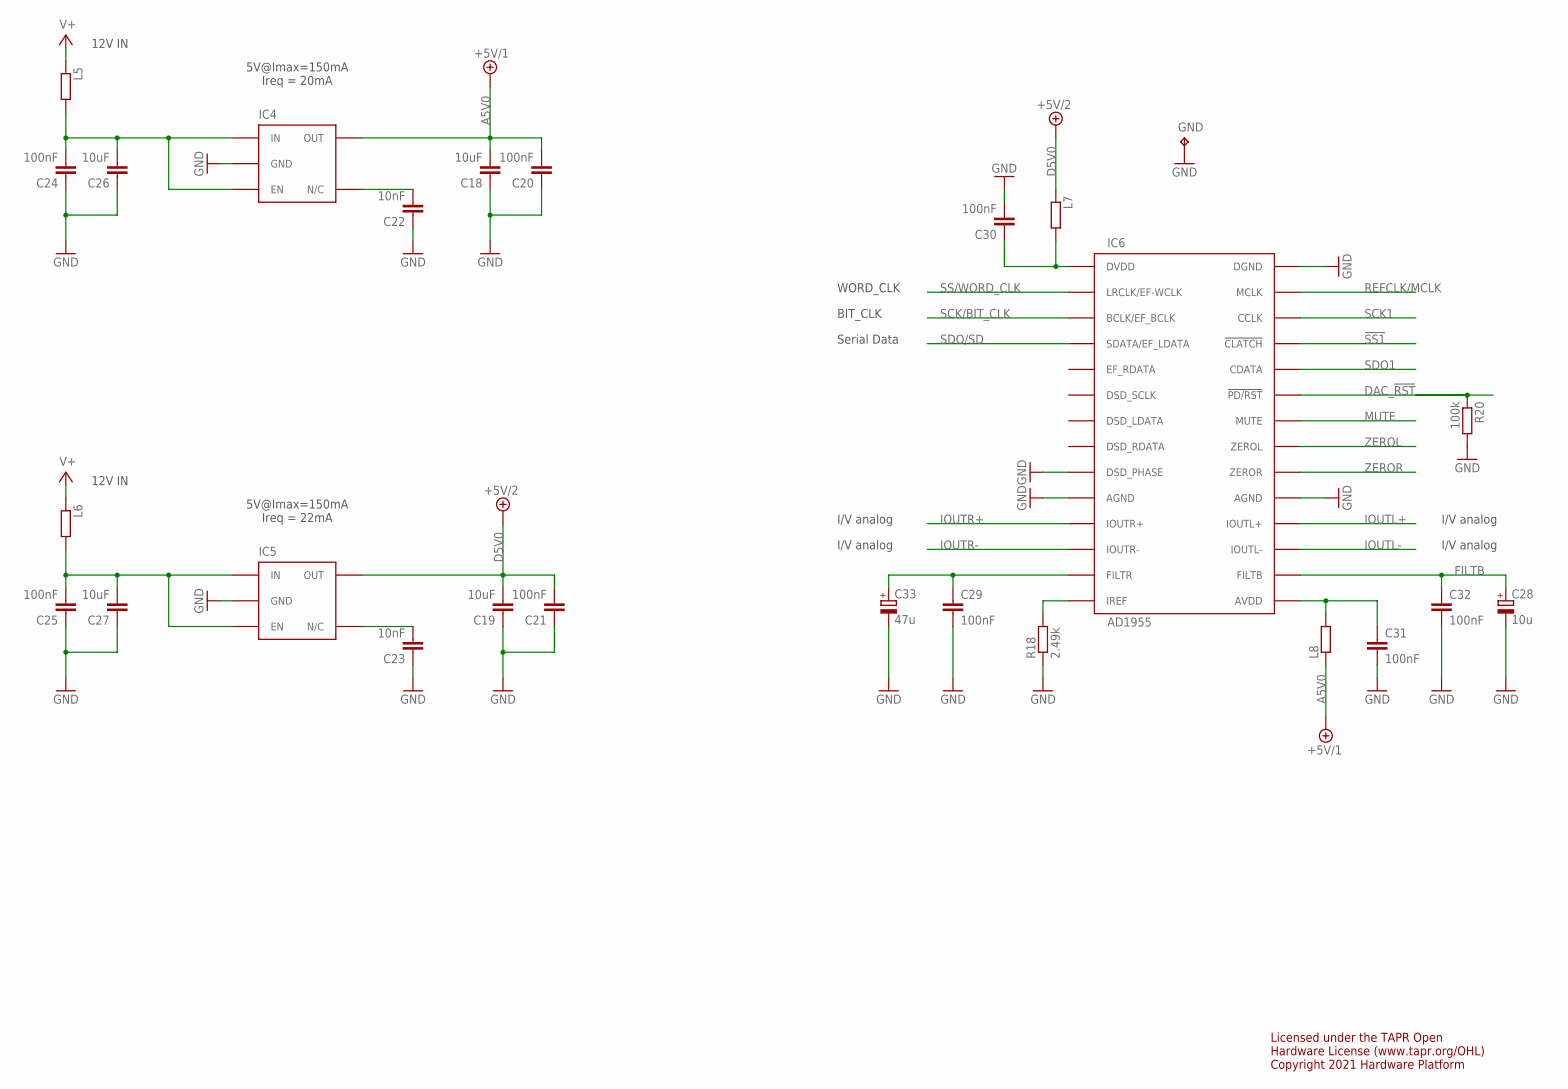
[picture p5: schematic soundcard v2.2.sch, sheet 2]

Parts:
C18, C19, C26, C27: 10uF; C0603
C20, C21, C24, C25, C29, C30, C31, C32: 100nF; C0402
C22, C23: 10nF; C0402
C28: 10u; B/3528-21W
C33: 47u; C/6032-28W
GND: TP; TP_1
IC4, IC5: LP5907MFX-3.3; TSOT23-5
IC6: AD1955; SSOP28
L5, L6, L7, L8: 600@100M; R0805
R18: 2.49k; R0402
R20: 100k; R0402

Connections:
!SS1: IC6.P25 (!CLATCH); also elsewhere on the board
A5V0: C18.2, C20.2, IC4.5 (OUT), L8.1; also elsewhere on the board
D5V0: C19.2, C21.2, IC5.5 (OUT), L7.1
DAC_!RST: IC6.P23 (!PD/RST), R20.1; also elsewhere on the board
FILTB: C28.+, C32.1, IC6.P16 (FILTB)
GND: C18.1, C19.1, C20.1, C21.1, C22.1, C23.1, C24.1, C25.1, C26.1, C27.1, C28.-, C29.2, C30.2, C31.2, C32.2, C33.-, GND.TP, IC4.2 (GND), IC5.2 (GND), IC6.P9 (DSD_PHASE), IC6.P10 (AGND), IC6.P19 (AGND), IC6.P28 (DGND), R18.1, R20.2; also elsewhere on the board
IOUTL+: IC6.P18 (IOUTL+); also elsewhere on the board
IOUTL-: IC6.P17 (IOUTL-); also elsewhere on the board
IOUTR+: IC6.P11 (IOUTR+); also elsewhere on the board
IOUTR-: IC6.P12 (IOUTR-); also elsewhere on the board
MUTE: IC6.P22 (MUTE); also elsewhere on the board
unnamed: C22.2, IC4.4 (N/C)
unnamed: C25.2, C27.2, IC5.1 (IN), IC5.3 (EN), L6.2
unnamed: C23.2, IC5.4 (N/C)
unnamed: C30.1, IC6.P1 (DVDD), L7.2
unnamed: C29.1, C33.+, IC6.P13 (FILTR)
unnamed: C31.1, IC6.P15 (AVDD), L8.2
unnamed: IC6.P14 (IREF), R18.2
unnamed: C24.2, C26.2, IC4.1 (IN), IC4.3 (EN), L5.2
REFCLK/MCLK: IC6.P27 (MCLK); also elsewhere on the board
SCK1: IC6.P26 (CCLK); also elsewhere on the board
SCK/BIT_CLK: IC6.P3 (BCLK/EF_BCLK); also elsewhere on the board
SDO1: IC6.P24 (CDATA); also elsewhere on the board
SDO/SD: IC6.P4 (SDATA/EF_LDATA); also elsewhere on the board
SS/WORD_CLK: IC6.P2 (LRCLK/EF-WCLK); also elsewhere on the board
V+: L5.1, L6.1; also elsewhere on the board
ZEROL: IC6.P21 (ZEROL); also elsewhere on the board
ZEROR: IC6.P20 (ZEROR); also elsewhere on the board

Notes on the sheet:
WORD_CLK
BIT_CLK
Serial Data
I/V analog
5V@Imax=150mA Ireq = 20mA
12V IN
Licensed under the TAPR Open Hardware License (www.tapr.org/OHL) Copyright 2021 Hardware Platform
5V@Imax=150mA Ireq = 22mA

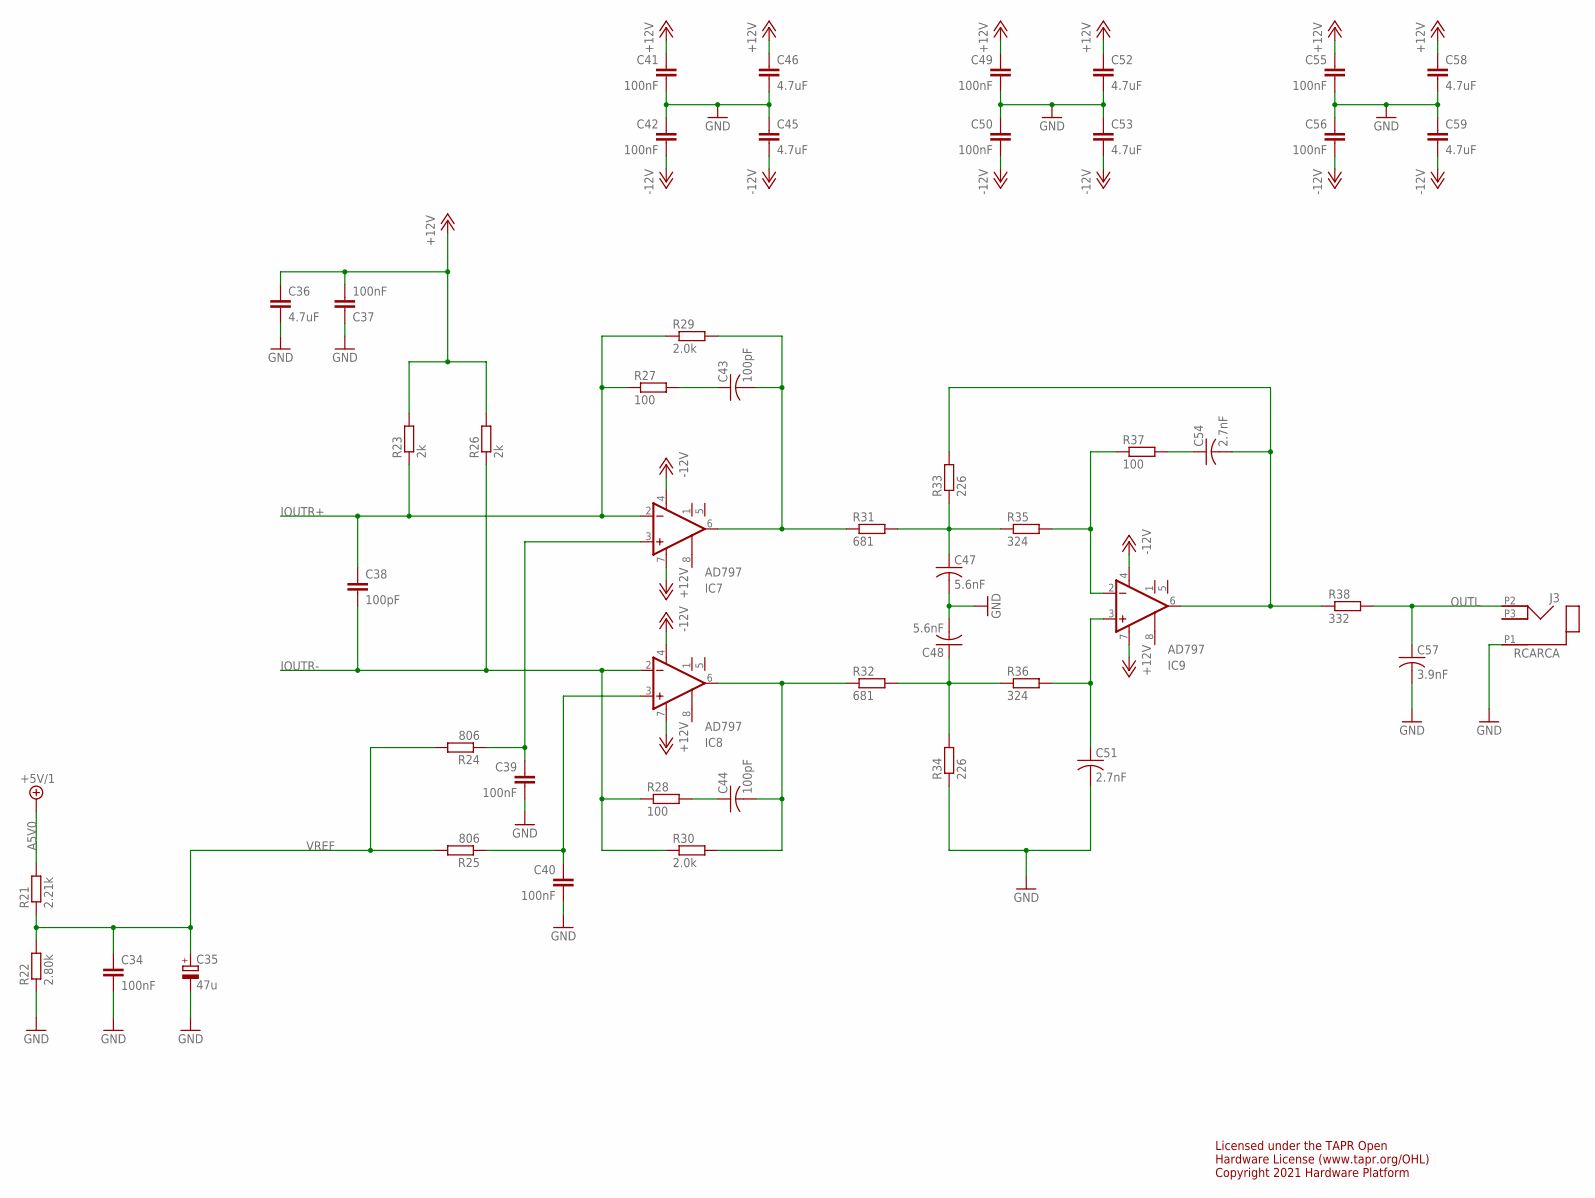
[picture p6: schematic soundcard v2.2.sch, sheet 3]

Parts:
C34, C37, C39, C40, C41, C42, C49, C50, C55, C56: 100nF; C0402
C35: 47u; C/6032-28W
C36, C45, C46, C52, C53, C58, C59: 4.7uF; C0603
C38: 100pF; C0603
C43, C44: 100pF; C050-025X075
C47, C48: 5.6nF; C050-025X075
C51, C54: 2.7nF; C050-025X075
C57: 3.9nF; C050-025X075
IC7, IC8, IC9: AD797; SO08
J3: RCARCA; RCA
R21: 2.21k; R0402
R22: 2.80k; R0402
R23, R26: 2k; R0402
R24, R25: 806; R0402
R27, R28, R37: 100; R0402
R29, R30: 2.0k; R0402
R31, R32: 681; R0402
R33, R34: 226; R0402
R35, R36: 324; R0402
R38: 332; R0402

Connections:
+12V: C36.1, C37.2, C41.1, C46.1, C49.1, C52.1, C55.1, C58.1, IC7.7 (V+), IC8.7 (V+), IC9.7 (V+), R23.2, R26.2; also elsewhere on the board
-12V: C42.2, C45.2, C50.2, C53.2, C56.2, C59.2, IC7.4 (V-), IC8.4 (V-), IC9.4 (V-); also elsewhere on the board
A5V0: R21.2; also elsewhere on the board
GND: C34.2, C35.-, C36.2, C37.1, C39.2, C40.2, C41.2, C42.1, C45.1, C46.2, C47.2, C48.2, C49.2, C50.1, C51.2, C52.2, C53.1, C55.2, C56.1, C57.2, C58.2, C59.1, J3.P1 (1), R22.1, R34.1; also elsewhere on the board
IOUTR+: C38.1, IC7.2 (-IN), R23.1, R27.1, R29.1; also elsewhere on the board
IOUTR-: C38.2, IC8.2 (-IN), R26.1, R28.1, R30.1; also elsewhere on the board
unnamed: C39.1, IC7.3 (+IN), R24.1
unnamed: C40.1, IC8.3 (+IN), R25.1
unnamed: C54.1, R37.2
unnamed: C44.2, IC8.6 (OUT), R30.2, R32.1
unnamed: C43.2, IC7.6 (OUT), R29.2, R31.1
unnamed: C47.1, R31.2, R33.1, R35.1
unnamed: C48.1, R32.2, R34.2, R36.1
unnamed: IC9.2 (-IN), R35.2, R37.1
unnamed: C51.1, IC9.3 (+IN), R36.2
unnamed: C54.2, IC9.6 (OUT), R33.2, R38.1
unnamed: C43.1, R27.2
unnamed: C44.1, R28.2
OUTL: C57.1, J3.P2 (2), R38.2
VREF: C34.1, C35.+, R21.1, R22.2, R24.2, R25.2; also elsewhere on the board

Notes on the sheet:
Licensed under the TAPR Open Hardware License (www.tapr.org/OHL) Copyright 2021 Hardware Platform

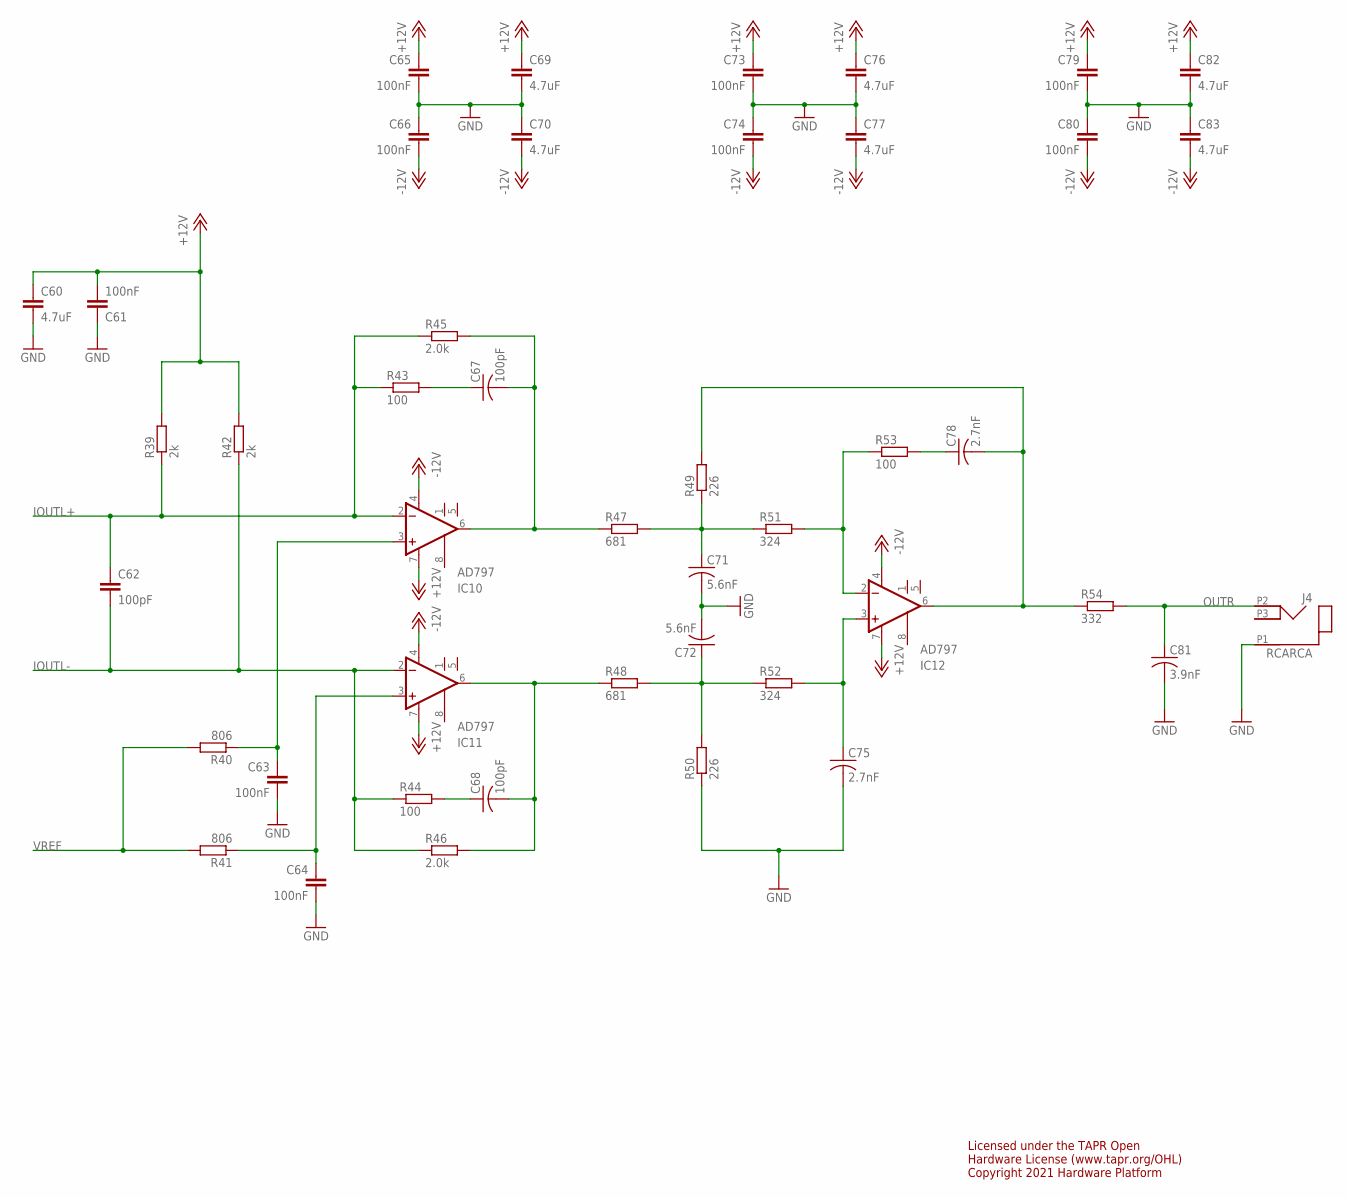
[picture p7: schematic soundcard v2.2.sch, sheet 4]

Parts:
C60, C69, C70, C76, C77, C82, C83: 4.7uF; C0603
C61, C63, C64, C65, C66, C73, C74, C79, C80: 100nF; C0402
C62: 100pF; C0603
C67, C68: 100pF; C050-025X075
C71, C72: 5.6nF; C050-025X075
C75, C78: 2.7nF; C050-025X075
C81: 3.9nF; C050-025X075
IC10, IC11, IC12: AD797; SO08
J4: RCARCA; RCA
R39, R42: 2k; R0402
R40, R41: 806; R0402
R43, R44, R53: 100; R0402
R45, R46: 2.0k; R0402
R47, R48: 681; R0402
R49, R50: 226; R0402
R51, R52: 324; R0402
R54: 332; R0402

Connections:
+12V: C60.1, C61.2, C65.1, C69.1, C73.1, C76.1, C79.1, C82.1, IC10.7 (V+), IC11.7 (V+), IC12.7 (V+), R39.2, R42.2; also elsewhere on the board
-12V: C66.2, C70.2, C74.2, C77.2, C80.2, C83.2, IC10.4 (V-), IC11.4 (V-), IC12.4 (V-); also elsewhere on the board
GND: C60.2, C61.1, C63.2, C64.2, C65.2, C66.1, C69.2, C70.1, C71.2, C72.2, C73.2, C74.1, C75.2, C76.2, C77.1, C79.2, C80.1, C81.2, C82.2, C83.1, J4.P1 (1), R50.1; also elsewhere on the board
IOUTL+: C62.1, IC10.2 (-IN), R39.1, R43.1, R45.1; also elsewhere on the board
IOUTL-: C62.2, IC11.2 (-IN), R42.1, R44.1, R46.1; also elsewhere on the board
unnamed: C63.1, IC10.3 (+IN), R40.1
unnamed: C67.2, IC10.6 (OUT), R45.2, R47.1
unnamed: C68.2, IC11.6 (OUT), R46.2, R48.1
unnamed: C71.1, R47.2, R49.1, R51.1
unnamed: C72.1, R48.2, R50.2, R52.1
unnamed: IC12.2 (-IN), R51.2, R53.1
unnamed: C75.1, IC12.3 (+IN), R52.2
unnamed: C78.2, IC12.6 (OUT), R49.2, R54.1
unnamed: C67.1, R43.2
unnamed: C68.1, R44.2
unnamed: C64.1, IC11.3 (+IN), R41.1
unnamed: C78.1, R53.2
OUTR: C81.1, J4.P2 (2), R54.2
VREF: R40.2, R41.2; also elsewhere on the board

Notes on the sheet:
Licensed under the TAPR Open Hardware License (www.tapr.org/OHL) Copyright 2021 Hardware Platform

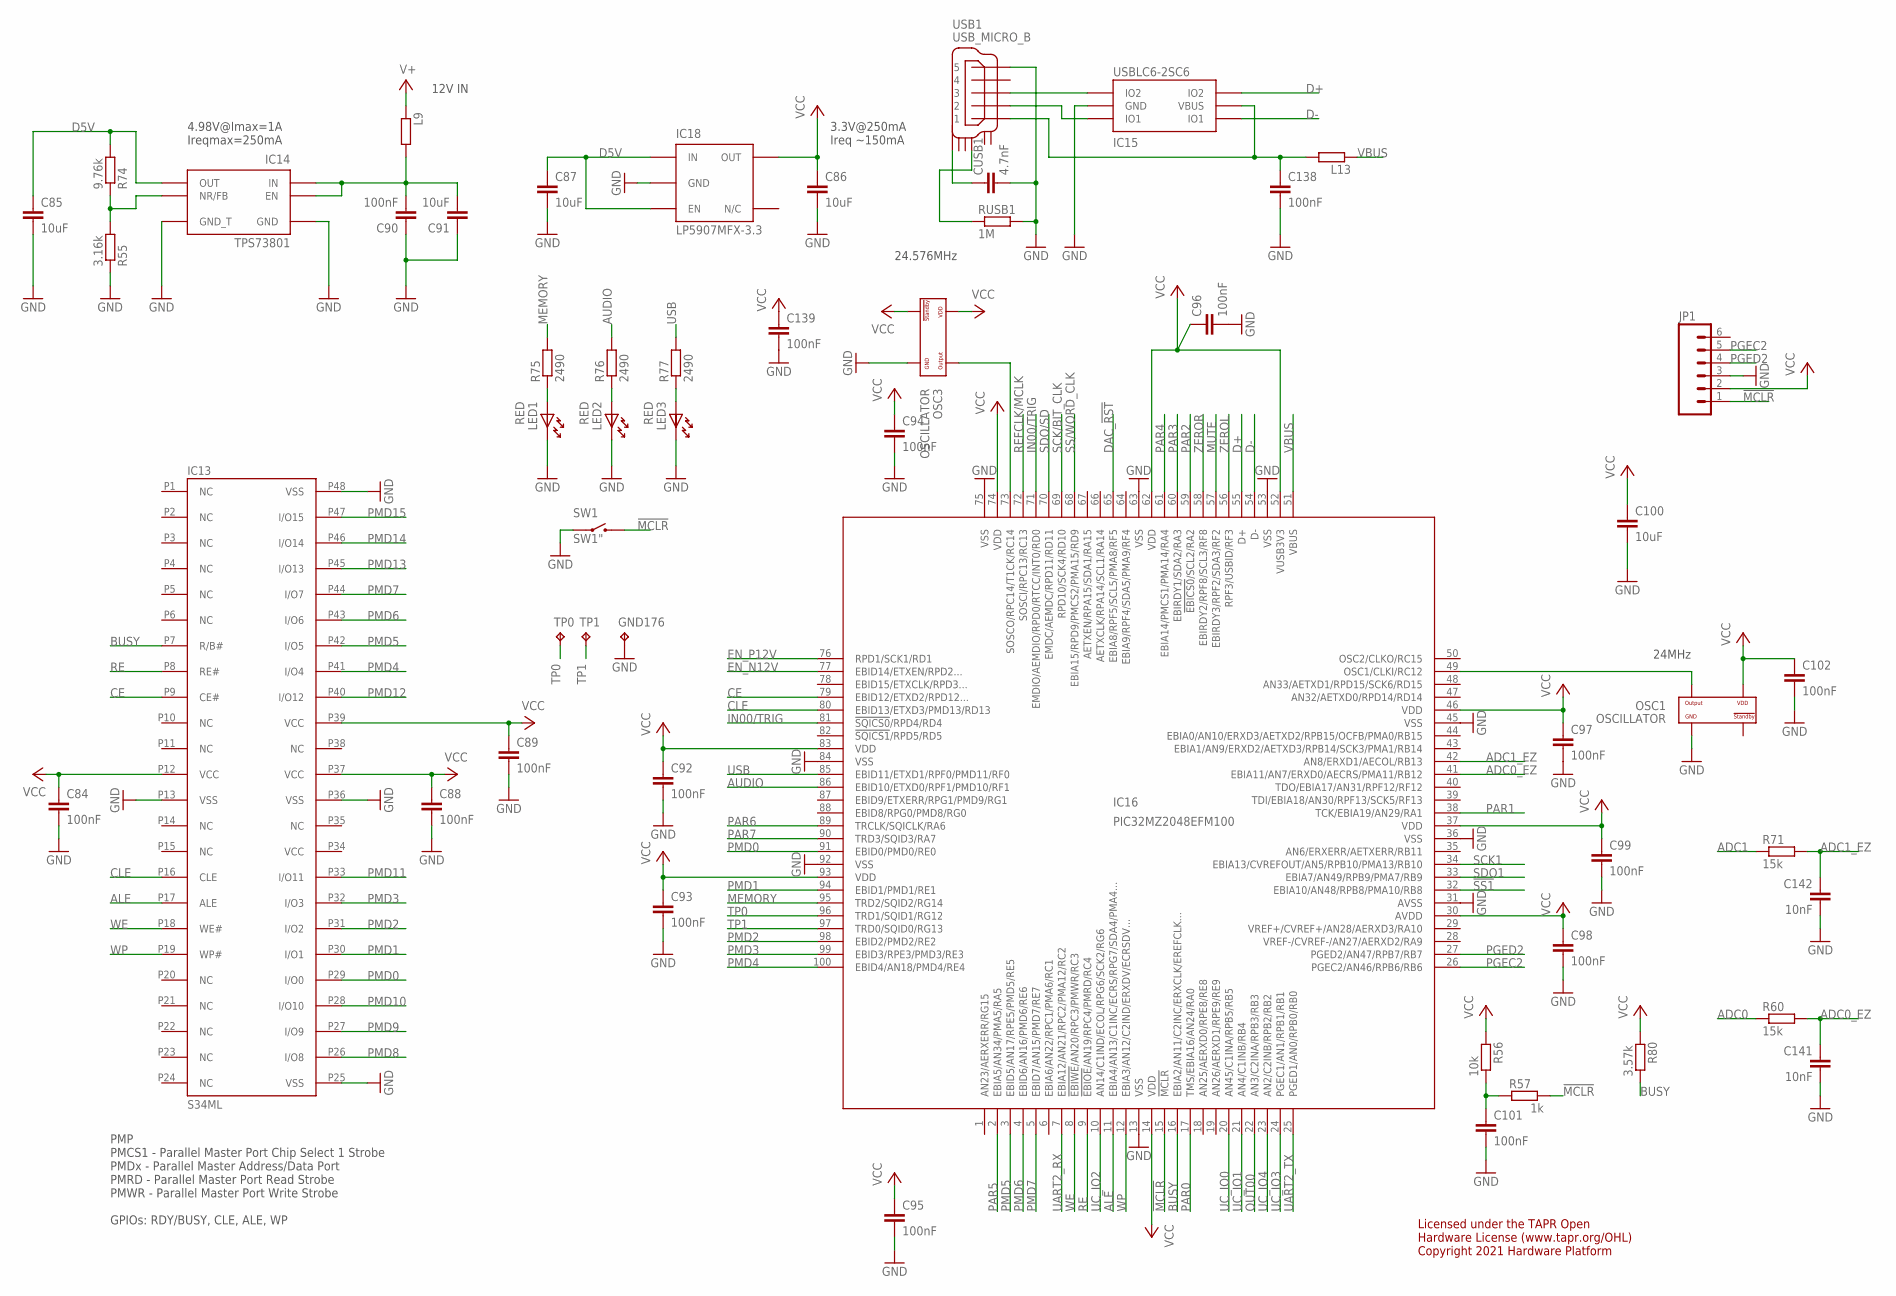
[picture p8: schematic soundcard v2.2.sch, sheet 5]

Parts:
C84, C88, C89, C90, C92, C93, C94, C95, C96, C97, C98, C99, C101, C102, C138, C139: 100nF; C0402
C85, C86, C87, C91, C100: 10uF; C0603
C141, C142: 10nF; C0402
CUSB1: 4.7nF; C0402
GND176: TP; TP_1
IC13: S34ML; TSOP-48
IC14: TPS73801; SOT223-6
IC15: USBLC6-2SC6; SOT23-6L
IC16: PIC32MZ2048EFM100; TQFP-100
IC18: LP5907MFX-3.3; TSOT23-5
JP1: M06NO_SILK; 1X06_NO_SILK
L9: 600@100M; R0805
L13: ???; R0805
LED1, LED2, LED3: RED; LED_HAND
OSC1, OSC3: OSCILLATOR; OSCILLATOR_3.2X2.5
R55: 3.16k; R0402
R56: 10k; R0402
R57: 1k; R0402
R60, R71: 15k; R0402
R74: 9.76k; R0402
R75, R76, R77: 2490; R0402
R80: 3.57k; R0402
RUSB1: 1M; R0402
SW1: SW1"; SWITCH_KSS
TP0, TP1: TP; TP_1
USB1: USB_MICRO_B; ZX62D-B-5P8

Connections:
!MCLR: IC16.15 (!MCLR), JP1.1, R57.1, SW1.O
!SS1: IC16.32 (EBIA10/AN48/RPB8/PMA10/RB8); also elsewhere on the board
ADC0: R60.1; also elsewhere on the board
ADC0_EZ: C141.1, IC16.41 (EBIA11/AN7/ERXD0/AECRS/PMA11/RB12), R60.2
ADC1: R71.1; also elsewhere on the board
ADC1_EZ: C142.1, IC16.42 (AN8/ERXD1/AECOL/RB13), R71.2
ALE: IC13.P17 (ALE), IC16.11 (EBIA4/AN13/C1INC/ECRS/RPG7/SDA4/PMA4...)
AUDIO: IC16.86 (EBID10/ETXD0/RPF1/PMD10/RF1), R76.2
BUSY: IC13.P7 (R/B#), IC16.16 (EBIA2/AN11/C2INC/ERXCLK/EREFCLK...), R80.1
CE: IC13.P9 (CE#), IC16.79 (EBID12/ETXD2/RPD12...)
CLE: IC13.P16 (CLE), IC16.80 (EBID13/ETXD3/PMD13/RD13)
D5V: C85.1, C87.1, IC14.P$2 (OUT), IC18.1 (IN), IC18.3 (EN), R74.2; also elsewhere on the board
D+: IC15.P$4 (IO2), IC16.55 (D+)
D-: IC15.P$6 (IO1), IC16.54 (D-)
DAC_!RST: IC16.65 (EBIA8/RPF5/SCL5/PMA8/RF5); also elsewhere on the board
EN_N12V: IC16.77 (EBID14/ETXEN/RPD2...); also elsewhere on the board
EN_P12V: IC16.76 (RPD1/SCK1/RD1); also elsewhere on the board
GND: C84.2, C85.2, C86.2, C87.2, C88.2, C89.2, C90.1, C91.1, C92.2, C93.2, C94.2, C95.2, C96.2, C97.2, C98.2, C99.2, C100.2, C101.2, C102.2, C138.2, C139.2, C141.2, C142.2, CUSB1.2, GND176.TP, IC13.P13 (VSS), IC13.P25 (VSS), IC13.P36 (VSS), IC13.P48 (VSS), IC14.P$3 (GND), IC14.P$6 (GND_T), IC15.P$2 (GND), IC16.13 (VSS), IC16.31 (AVSS), IC16.36 (VSS), IC16.45 (VSS), IC16.53 (VSS), IC16.63 (VSS), IC16.75 (VSS), IC16.84 (VSS), IC16.92 (VSS), IC18.2 (GND), JP1.3, LED1.K, LED2.K, LED3.K, OSC1.P$2 (GND), OSC3.P$2 (GND), R55.1, RUSB1.2, SW1.P, USB1.P$5 (5); also elsewhere on the board
IN00/TRIG: IC16.71 (EMDIO/AEMDIO/RPD0/RTCC/INT0/RD0), IC16.81 (!SQICS0!/RPD4/RD4); also elsewhere on the board
MEMORY: IC16.95 (TRD2/SQID2/RG14), R75.2
MUTE: IC16.57 (EBIRDY3/RPF2/SDA3/RF2); also elsewhere on the board
unnamed: IC14.P$4 (NR/FB), R55.2, R74.1
unnamed: C90.2, C91.2, IC14.P$1 (IN), IC14.P$5 (EN), L9.2
unnamed: IC16.73 (SOSCO/RPC14/T1CK/RC14), OSC3.P$3 (OUTPUT)
unnamed: LED1.A, R75.1
unnamed: LED2.A, R76.1
unnamed: LED3.A, R77.1
unnamed: IC16.49 (OSC1/CLKI/RC12), OSC1.P$3 (OUTPUT)
unnamed: IC15.P$1 (IO1), USB1.P$2 (2)
unnamed: IC15.P$3 (IO2), USB1.P$3 (3)
unnamed: CUSB1.1, USB1.SHIELD_4
unnamed: RUSB1.1, USB1.SHIELD_3
unnamed: C101.1, R56.1, R57.2
OUT00: IC16.22 (AN3/C2INA/RPB3/RB3); also elsewhere on the board
PAR0: IC16.17 (TMS/EBIA16/AN24/RA0); also elsewhere on the board
PAR1: IC16.38 (TCK/EBIA19/AN29/RA1); also elsewhere on the board
PAR2: IC16.59 (!EBICS0!/SCL2/RA2); also elsewhere on the board
PAR3: IC16.60 (EBIRDY1/SDA2/RA3); also elsewhere on the board
PAR4: IC16.61 (EBIA14/PMCS1/PMA14/RA4); also elsewhere on the board
PAR5: IC16.2 (EBIA5/AN34/PMA5/RA5); also elsewhere on the board
PAR6: IC16.89 (TRCLK/SQICLK/RA6); also elsewhere on the board
PAR7: IC16.90 (TRD3/SQID3/RA7); also elsewhere on the board
PGEC2: IC16.26 (PGEC2/AN46/RPB6/RB6), JP1.5
PGED2: IC16.27 (PGED2/AN47/RPB7/RB7), JP1.4
PMD0: IC13.P29 (I/O0), IC16.91 (EBID0/PMD0/RE0)
PMD1: IC13.P30 (I/O1), IC16.94 (EBID1/PMD1/RE1)
PMD2: IC13.P31 (I/O2), IC16.98 (EBID2/PMD2/RE2)
PMD3: IC13.P32 (I/O3), IC16.99 (EBID3/RPE3/PMD3/RE3)
PMD4: IC13.P41 (I/O4), IC16.100 (EBID4/AN18/PMD4/RE4)
PMD5: IC13.P42 (I/O5), IC16.3 (EBID5/AN17/RPE5/PMD5/RE5)
PMD6: IC13.P43 (I/O6), IC16.4 (EBID6/AN16/PMD6/RE6)
PMD7: IC13.P44 (I/O7), IC16.5 (EBID7/AN15/PMD7/RE7)
PMD8: IC13.P26 (I/O8)
PMD9: IC13.P27 (I/O9)
PMD10: IC13.P28 (I/O10)
PMD11: IC13.P33 (I/O11)
PMD12: IC13.P40 (I/O12)
PMD13: IC13.P45 (I/O13)
PMD14: IC13.P46 (I/O14)
PMD15: IC13.P47 (I/O15)
RE: IC13.P8 (RE#), IC16.9 (!EBIOE!/AN19/RPC4/PMRD/RC4)
REFCLK/MCLK: IC16.72 (SOSCI/RPC13/RC13); also elsewhere on the board
SCK1: IC16.34 (EBIA13/CVREFOUT/AN5/RPB10/PMA13/RB10); also elsewhere on the board
SCK/BIT_CLK: IC16.69 (RPD10/SCK4/RD10); also elsewhere on the board
SDO1: IC16.33 (EBIA7/AN49/RPB9/PMA7/RB9); also elsewhere on the board
SDO/SD: IC16.70 (EMDC/AEMDC/RPD11/RD11); also elsewhere on the board
SS/WORD_CLK: IC16.68 (EBIA15/RPD9/PMCS2/PMA15/RD9); also elsewhere on the board
TP0: IC16.96 (TRD1/SQID1/RG12), TP0.TP
TP1: IC16.97 (TRD0/SQID0/RG13), TP1.TP
UART2_RX: IC16.7 (EBIA12/AN21/RPC2/PMA12/RC2); also elsewhere on the board
UART2_TX: IC16.25 (PGED1/AN0/RPB0/RB0); also elsewhere on the board
UC_IO0: IC16.20 (AN45/C1INA/RPB5/RB5); also elsewhere on the board
UC_IO1: IC16.21 (AN4/C1INB/RB4); also elsewhere on the board
UC_IO2: IC16.10 (AN14/C1IND/ECOL/RPG6/SCK2/RG6); also elsewhere on the board
UC_IO3: IC16.24 (PGEC1/AN1/RPB1/RB1); also elsewhere on the board
UC_IO4: IC16.23 (AN2/C2INB/RPB2/RB2); also elsewhere on the board
USB: IC16.85 (EBID11/ETXD1/RPF0/PMD11/RF0), R77.2
V+: L9.1; also elsewhere on the board
VBUS: IC16.51 (VBUS), L13.1
VBUSX: C138.1, IC15.P$5 (VBUS), L13.2, USB1.P$1 (1)
VCC: C84.1, C86.1, C88.1, C89.1, C92.1, C93.1, C94.1, C95.1, C96.1, C97.1, C98.1, C99.1, C100.1, C102.1, C139.1, IC13.P12 (VCC), IC13.P37 (VCC), IC13.P39 (VCC), IC16.14 (VDD), IC16.30 (AVDD), IC16.37 (VDD), IC16.46 (VDD), IC16.52 (VUSB3V3), IC16.62 (VDD), IC16.74 (VDD), IC16.83 (VDD), IC16.93 (VDD), IC18.5 (OUT), JP1.2, OSC1.P$4 (VDD), OSC3.P$1 (STANDBY#), OSC3.P$4 (VDD), R56.2, R80.2
WE: IC13.P18 (WE#), IC16.8 (!EBIWE!/AN20/RPC3/PMWR/RC3)
WP: IC13.P19 (WP#), IC16.12 (EBIA3/AN12/C2IND/ERXDV/ECRSDV...)
ZEROL: IC16.56 (RPF3/USBID/RF3); also elsewhere on the board
ZEROR: IC16.58 (EBIRDY2/RPF8/SCL3/RF8); also elsewhere on the board

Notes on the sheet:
PMP PMCS1 - Parallel Master Port Chip Select 1 Strobe PMDx - Parallel Master Address/Data Port PMRD - Parallel Master Port Read Strobe PMWR - Parallel Master Port Write Strobe GPIOs: RDY/BUSY, CLE, ALE, WP
12V IN
4.98V@Imax=1A Ireqmax=250mA
3.3V@250mA Ireq ~150mA
24.576MHz
24MHz
Licensed under the TAPR Open Hardware License (www.tapr.org/OHL) Copyright 2021 Hardware Platform

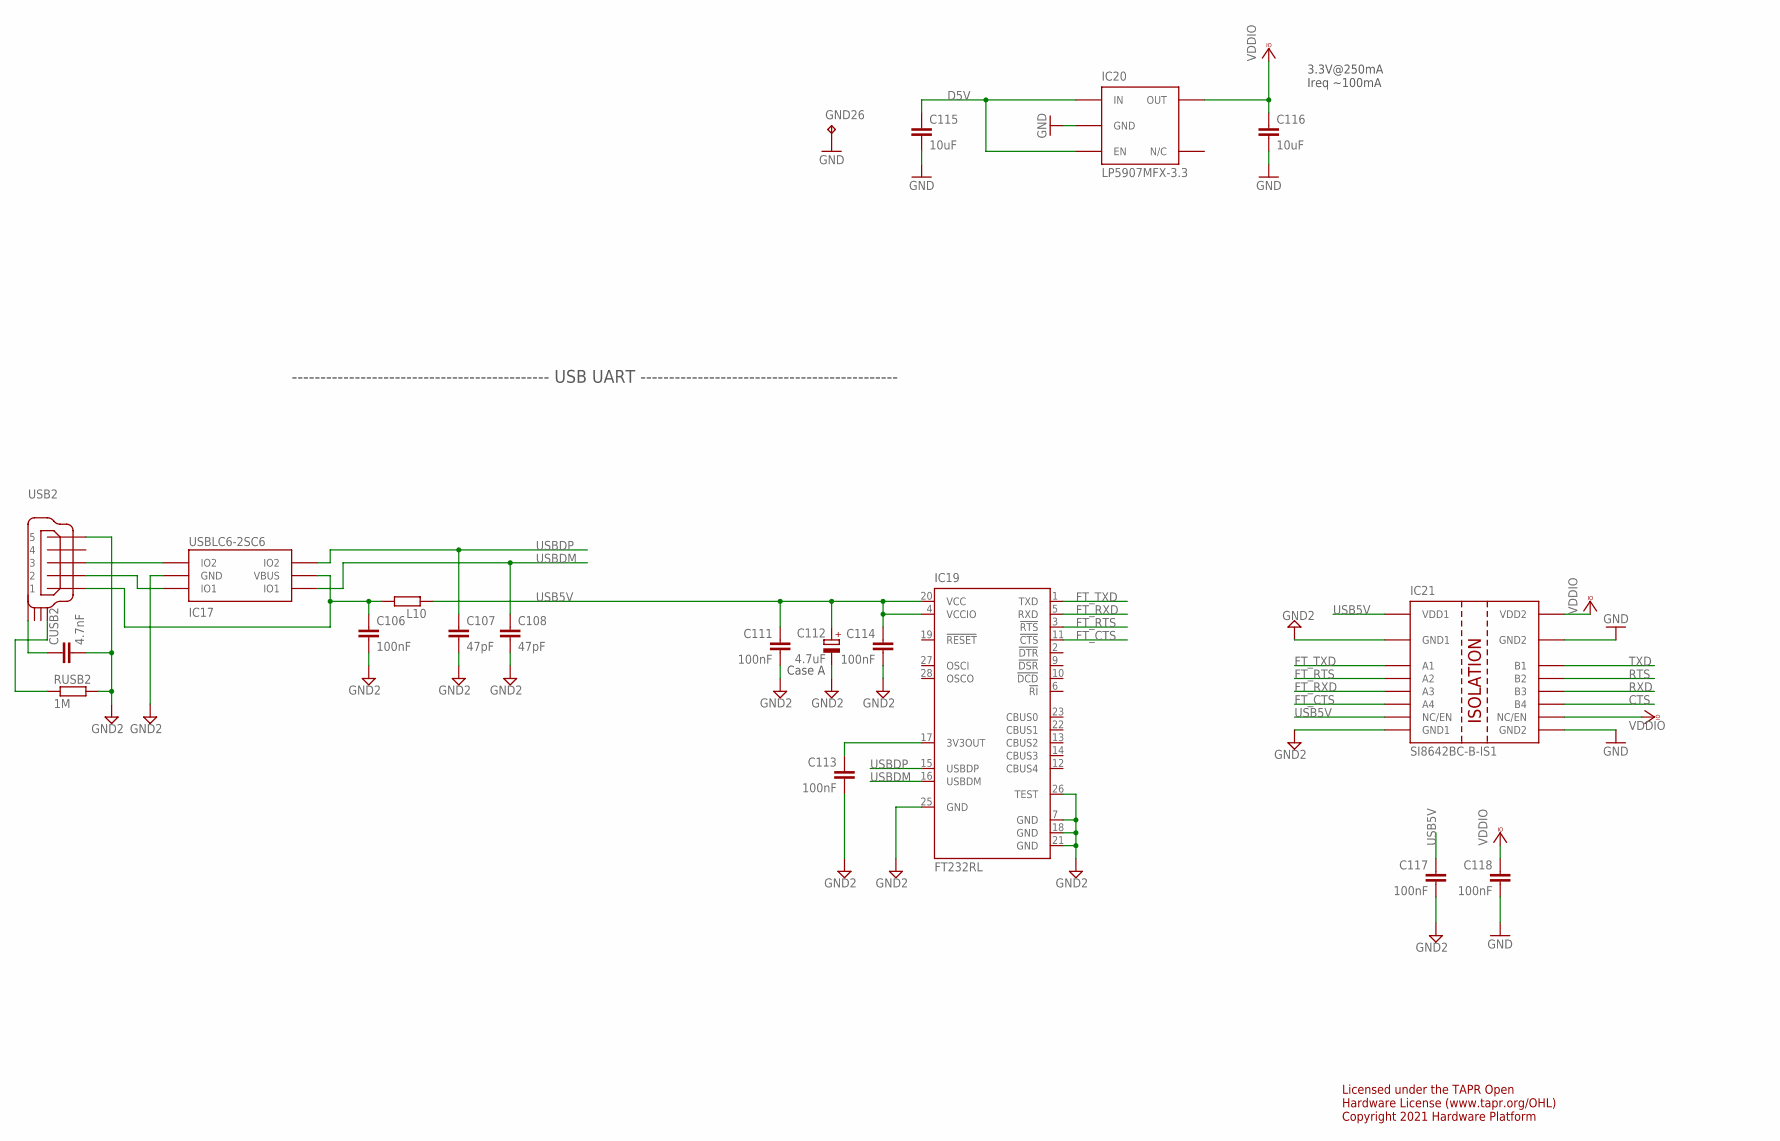
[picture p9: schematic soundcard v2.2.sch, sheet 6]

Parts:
C106, C111, C113, C114, C117, C118: 100nF; C0402
C107, C108: 47pF; C0402
C112: 4.7uF; A/3216-18W
C115, C116: 10uF; C0603
CUSB2: 4.7nF; C0402
GND26: TP; TP_1
IC17: USBLC6-2SC6; SOT23-6L
IC19: FT232RL; SSOP28
IC20: LP5907MFX-3.3; TSOT23-5
IC21: SI8642BC-B-IS1; NSOIC-16
L10: ???; R0805
RUSB2: 1M; R0402
USB2: USB_MINI_B; 240-0002-1

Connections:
CTS: IC21.11 (B4); also elsewhere on the board
D5V: C115.1, IC20.1 (IN), IC20.3 (EN); also elsewhere on the board
FT_CTS: IC19.11 (!CTS), IC21.6 (A4)
FT_RTS: IC19.3 (!RTS), IC21.4 (A2)
FT_RXD: IC19.5 (RXD), IC21.5 (A3)
FT_TXD: IC19.1 (TXD), IC21.3 (A1)
GND: C115.2, C116.2, C118.2, GND26.TP, IC20.2 (GND), IC21.9 (GND2), IC21.15 (GND2); also elsewhere on the board
GND2: C106.2, C107.2, C108.2, C111.2, C112.-, C113.2, C114.2, C117.2, CUSB2.2, IC17.P$2 (GND), IC19.7 (GND), IC19.18 (GND), IC19.21 (GND), IC19.25 (GND), IC19.26 (TEST), IC21.2 (GND1), IC21.8 (GND1), RUSB2.2, USB2.P$5 (5)
unnamed: C113.1, IC19.17 (3V3OUT)
unnamed: C106.1, IC17.P$5 (VBUS), L10.2, USB2.P$1 (1)
unnamed: IC17.P$1 (IO1), USB2.P$2 (2)
unnamed: IC17.P$3 (IO2), USB2.P$3 (3)
unnamed: CUSB2.1, USB2.SHIELD_4
unnamed: RUSB2.1, USB2.SHIELD_1
RTS: IC21.13 (B2); also elsewhere on the board
RXD: IC21.12 (B3); also elsewhere on the board
TXD: IC21.14 (B1); also elsewhere on the board
USB5V: C111.1, C112.+, C114.1, C117.1, IC19.4 (VCCIO), IC19.20 (VCC), IC21.1 (VDD1), IC21.7 (NC/EN), L10.1
USBDM: C108.1, IC17.P$6 (IO1), IC19.16 (USBDM)
USBDP: C107.1, IC17.P$4 (IO2), IC19.15 (USBDP)
VCCIO: C116.1, C118.1, IC20.5 (OUT), IC21.10 (NC/EN), IC21.16 (VDD2); also elsewhere on the board

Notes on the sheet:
Case A
--------------------------------------------- USB UART ---------------------------------------------
3.3V@250mA Ireq ~100mA
Licensed under the TAPR Open Hardware License (www.tapr.org/OHL) Copyright 2021 Hardware Platform

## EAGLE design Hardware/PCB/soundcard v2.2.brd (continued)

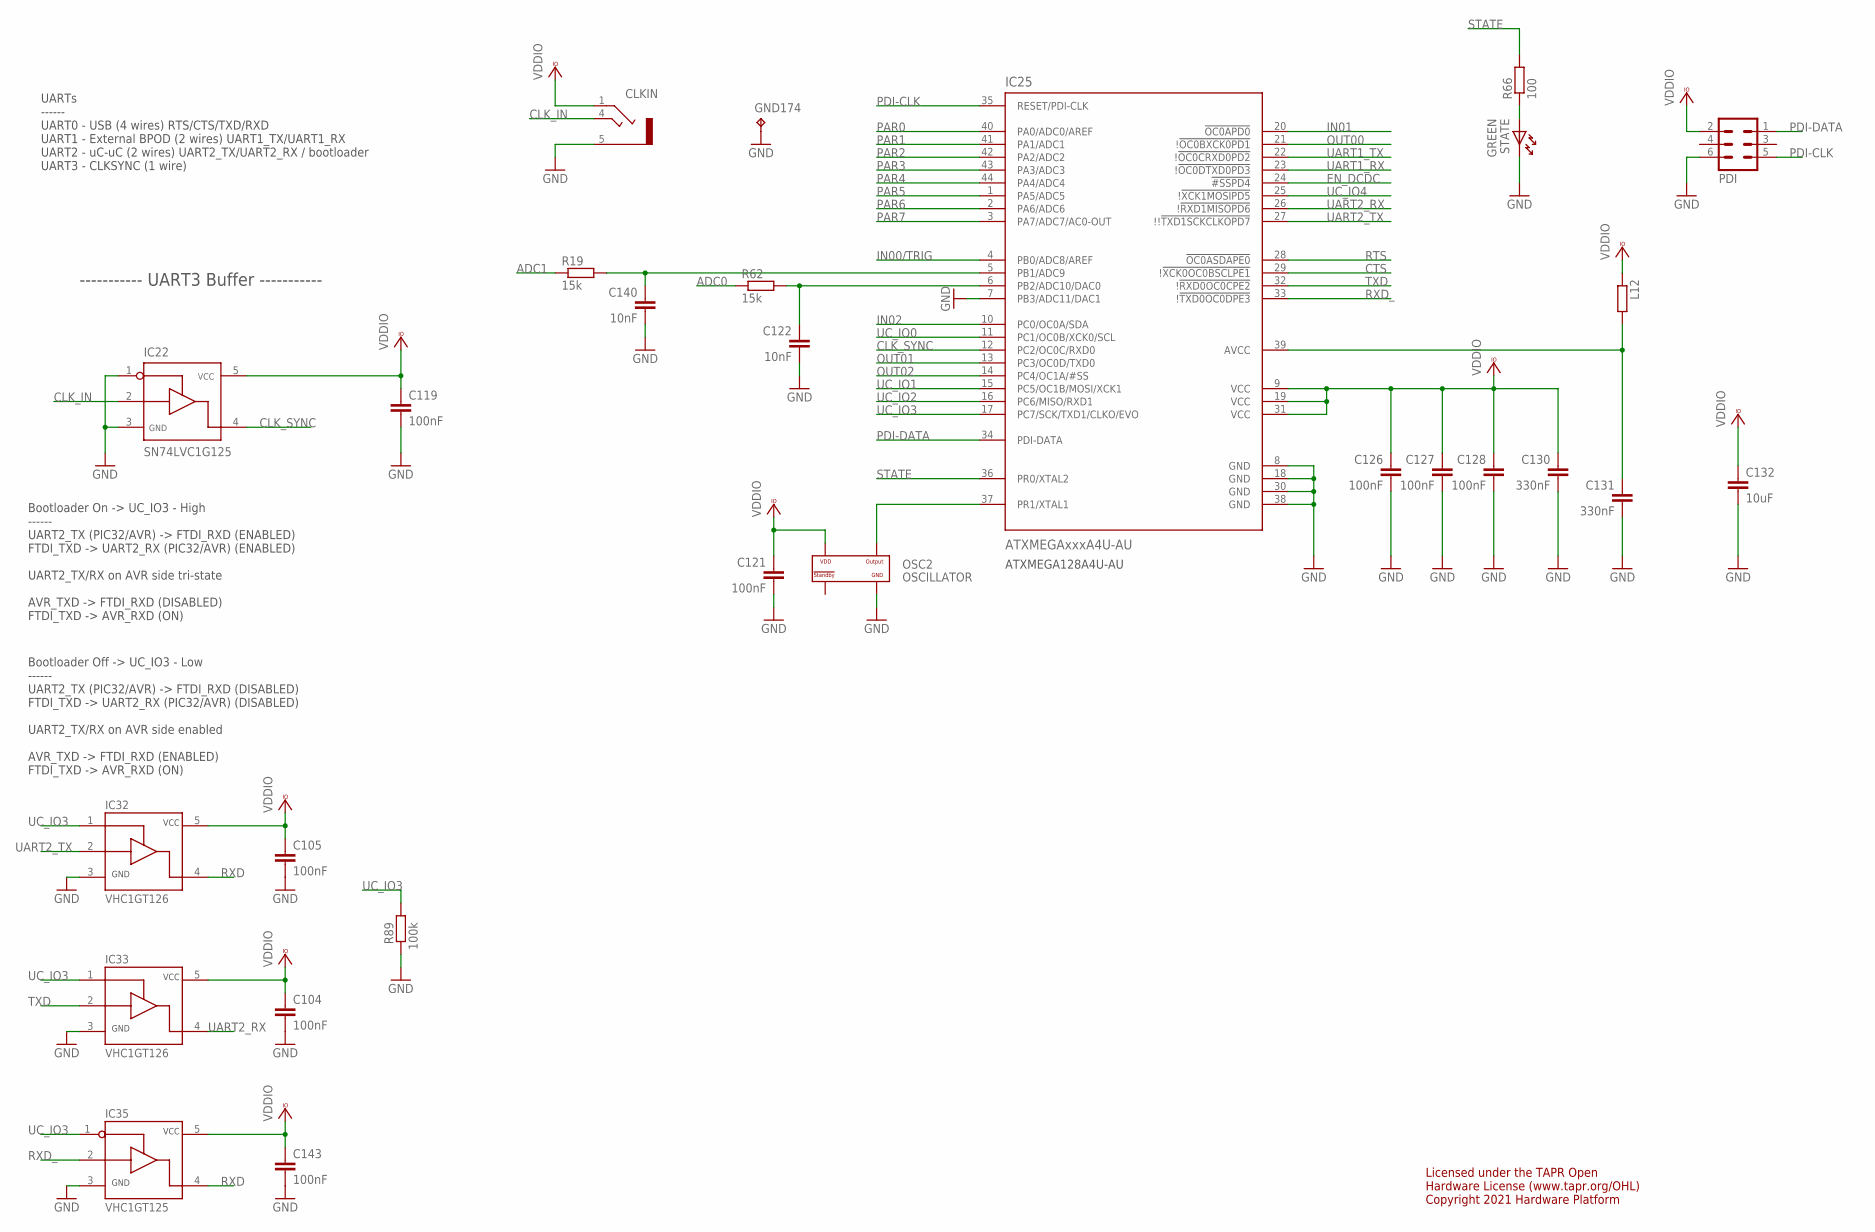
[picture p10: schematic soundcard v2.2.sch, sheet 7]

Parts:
C104, C105, C119, C121, C126, C127, C128, C143: 100nF; C0402
C122, C140: 10nF; C0402
C130, C131: 330nF; C0402
C132: 10uF; C0603
CLKIN: STEREO_JACK; 35RASMT2BHNTRX
GND174: TP; TP_1
IC22: SN74LVC1G125; SOT23-5
IC25: ATXMEGAxxxA4U-AU; QFP80P1200X1200X120-44N
IC32, IC33: VHC1GT126; SC-70-5
IC35: VHC1GT125; SC-70-5
L12: ???; R0805
OSC2: OSCILLATOR; OSCILLATOR_3.2X2.5
PDI: MA03-2
R19, R62: 15k; R0402
R66: 100; R0402
R89: 100k; R0402
STATE: GREEN; LED_HAND

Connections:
A+3V3: C131.1, IC25.39 (AVCC), L12.2
ADC0: R62.1; also elsewhere on the board
ADC1: R19.1; also elsewhere on the board
CLK_IN: CLKIN.4, IC22.2
CLK_SYNC: IC22.4, IC25.12 (PC2/OC0C/RXD0)
CTS: IC25.29 (!!XCK0OC0BSCLPE1); also elsewhere on the board
EN_DCDC: IC25.24 (!#SSPD4); also elsewhere on the board
GND: C104.2, C105.2, C119.2, C121.2, C122.2, C126.2, C127.2, C128.2, C130.2, C131.2, C132.2, C140.2, C143.2, CLKIN.5, GND174.TP, IC22.1, IC22.3, IC25.7 (PB3/ADC11/DAC1), IC25.8 (GND), IC25.18 (GND), IC25.30 (GND), IC25.38 (GND), IC32.3 (GND), IC33.3 (GND), IC35.3 (GND), OSC2.P$2 (GND), PDI.6, R89.2, STATE.K; also elsewhere on the board
IN00/TRIG: IC25.4 (PB0/ADC8/AREF); also elsewhere on the board
IN01: IC25.20 (!OC0APD0); also elsewhere on the board
IN02: IC25.10 (PC0/OC0A/SDA); also elsewhere on the board
unnamed: C140.1, IC25.5 (PB1/ADC9), R19.2
unnamed: C122.1, IC25.6 (PB2/ADC10/DAC0), R62.2
unnamed: R66.1, STATE.A
OSC1: IC25.37 (PR1/XTAL1), OSC2.P$3 (OUTPUT)
OUT00: IC25.21 (!!OC0BXCK0PD1); also elsewhere on the board
OUT01: IC25.13 (PC3/OC0D/TXD0); also elsewhere on the board
OUT02: IC25.14 (PC4/OC1A/#SS); also elsewhere on the board
PAR0: IC25.40 (PA0/ADC0/AREF); also elsewhere on the board
PAR1: IC25.41 (PA1/ADC1); also elsewhere on the board
PAR2: IC25.42 (PA2/ADC2); also elsewhere on the board
PAR3: IC25.43 (PA3/ADC3); also elsewhere on the board
PAR4: IC25.44 (PA4/ADC4); also elsewhere on the board
PAR5: IC25.1 (PA5/ADC5); also elsewhere on the board
PAR6: IC25.2 (PA6/ADC6); also elsewhere on the board
PAR7: IC25.3 (PA7/ADC7/AC0-OUT); also elsewhere on the board
PDI-CLK: IC25.35 (RESET/PDI-CLK), PDI.5
PDI-DATA: IC25.34 (PDI-DATA), PDI.1
RTS: IC25.28 (!OC0ASDAPE0); also elsewhere on the board
RXD: IC32.4 (OUT), IC35.4 (OUT); also elsewhere on the board
RXD_: IC25.33 (!!TXD0OC0DPE3), IC35.2 (IN)
STATE: IC25.36 (PR0/XTAL2), R66.2
TXD: IC25.32 (!!RXD0OC0CPE2), IC33.2 (IN); also elsewhere on the board
UART1_RX: IC25.23 (!!OC0DTXD0PD3)
UART1_TX: IC25.22 (!!OC0CRXD0PD2)
UART2_RX: IC25.26 (!!RXD1MISOPD6), IC33.4 (OUT); also elsewhere on the board
UART2_TX: IC25.27 (!!!TXD1SCKCLKOPD7), IC32.2 (IN); also elsewhere on the board
UC_IO0: IC25.11 (PC1/OC0B/XCK0/SCL); also elsewhere on the board
UC_IO1: IC25.15 (PC5/OC1B/MOSI/XCK1); also elsewhere on the board
UC_IO2: IC25.16 (PC6/MISO/RXD1); also elsewhere on the board
UC_IO3: IC25.17 (PC7/SCK/TXD1/CLKO/EVO), IC32.1 (OE), IC33.1 (OE), IC35.1 (!OE), R89.1; also elsewhere on the board
UC_IO4: IC25.25 (!!XCK1MOSIPD5); also elsewhere on the board
VCCIO: C104.1, C105.1, C119.1, C121.1, C126.1, C127.1, C128.1, C130.1, C132.1, C143.1, CLKIN.1, IC22.5, IC25.9 (VCC), IC25.19 (VCC), IC25.31 (VCC), IC32.5 (VCC), IC33.5 (VCC), IC35.5 (VCC), L12.1, OSC2.P$4 (VDD), PDI.2; also elsewhere on the board

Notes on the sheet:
UARTs ------ UART0 - USB (4 wires) RTS/CTS/TXD/RXD UART1 - External BPOD (2 wires) UART1_TX/UART1_RX UART2 - uC-uC (2 wires) UART2_TX/UART2_RX / bootloader UART3 - CLKSYNC (1 wire)
----------- UART3 Buffer -----------
ATXMEGA128A4U-AU
Bootloader On -> UC_IO3 - High ------ UART2_TX (PIC32/AVR) -> FTDI_RXD (ENABLED) FTDI_TXD -> UART2_RX (PIC32/AVR) (ENABLED) UART2_TX/RX on AVR side tri-state AVR_TXD -> FTDI_RXD (DISABLED) FTDI_TXD -> AVR_RXD (ON)
Bootloader Off -> UC_IO3 - Low ------ UART2_TX (PIC32/AVR) -> FTDI_RXD (DISABLED) FTDI_TXD -> UART2_RX (PIC32/AVR) (DISABLED) UART2_TX/RX on AVR side enabled AVR_TXD -> FTDI_RXD (ENABLED) FTDI_TXD -> AVR_RXD (ON)
Licensed under the TAPR Open Hardware License (www.tapr.org/OHL) Copyright 2021 Hardware Platform

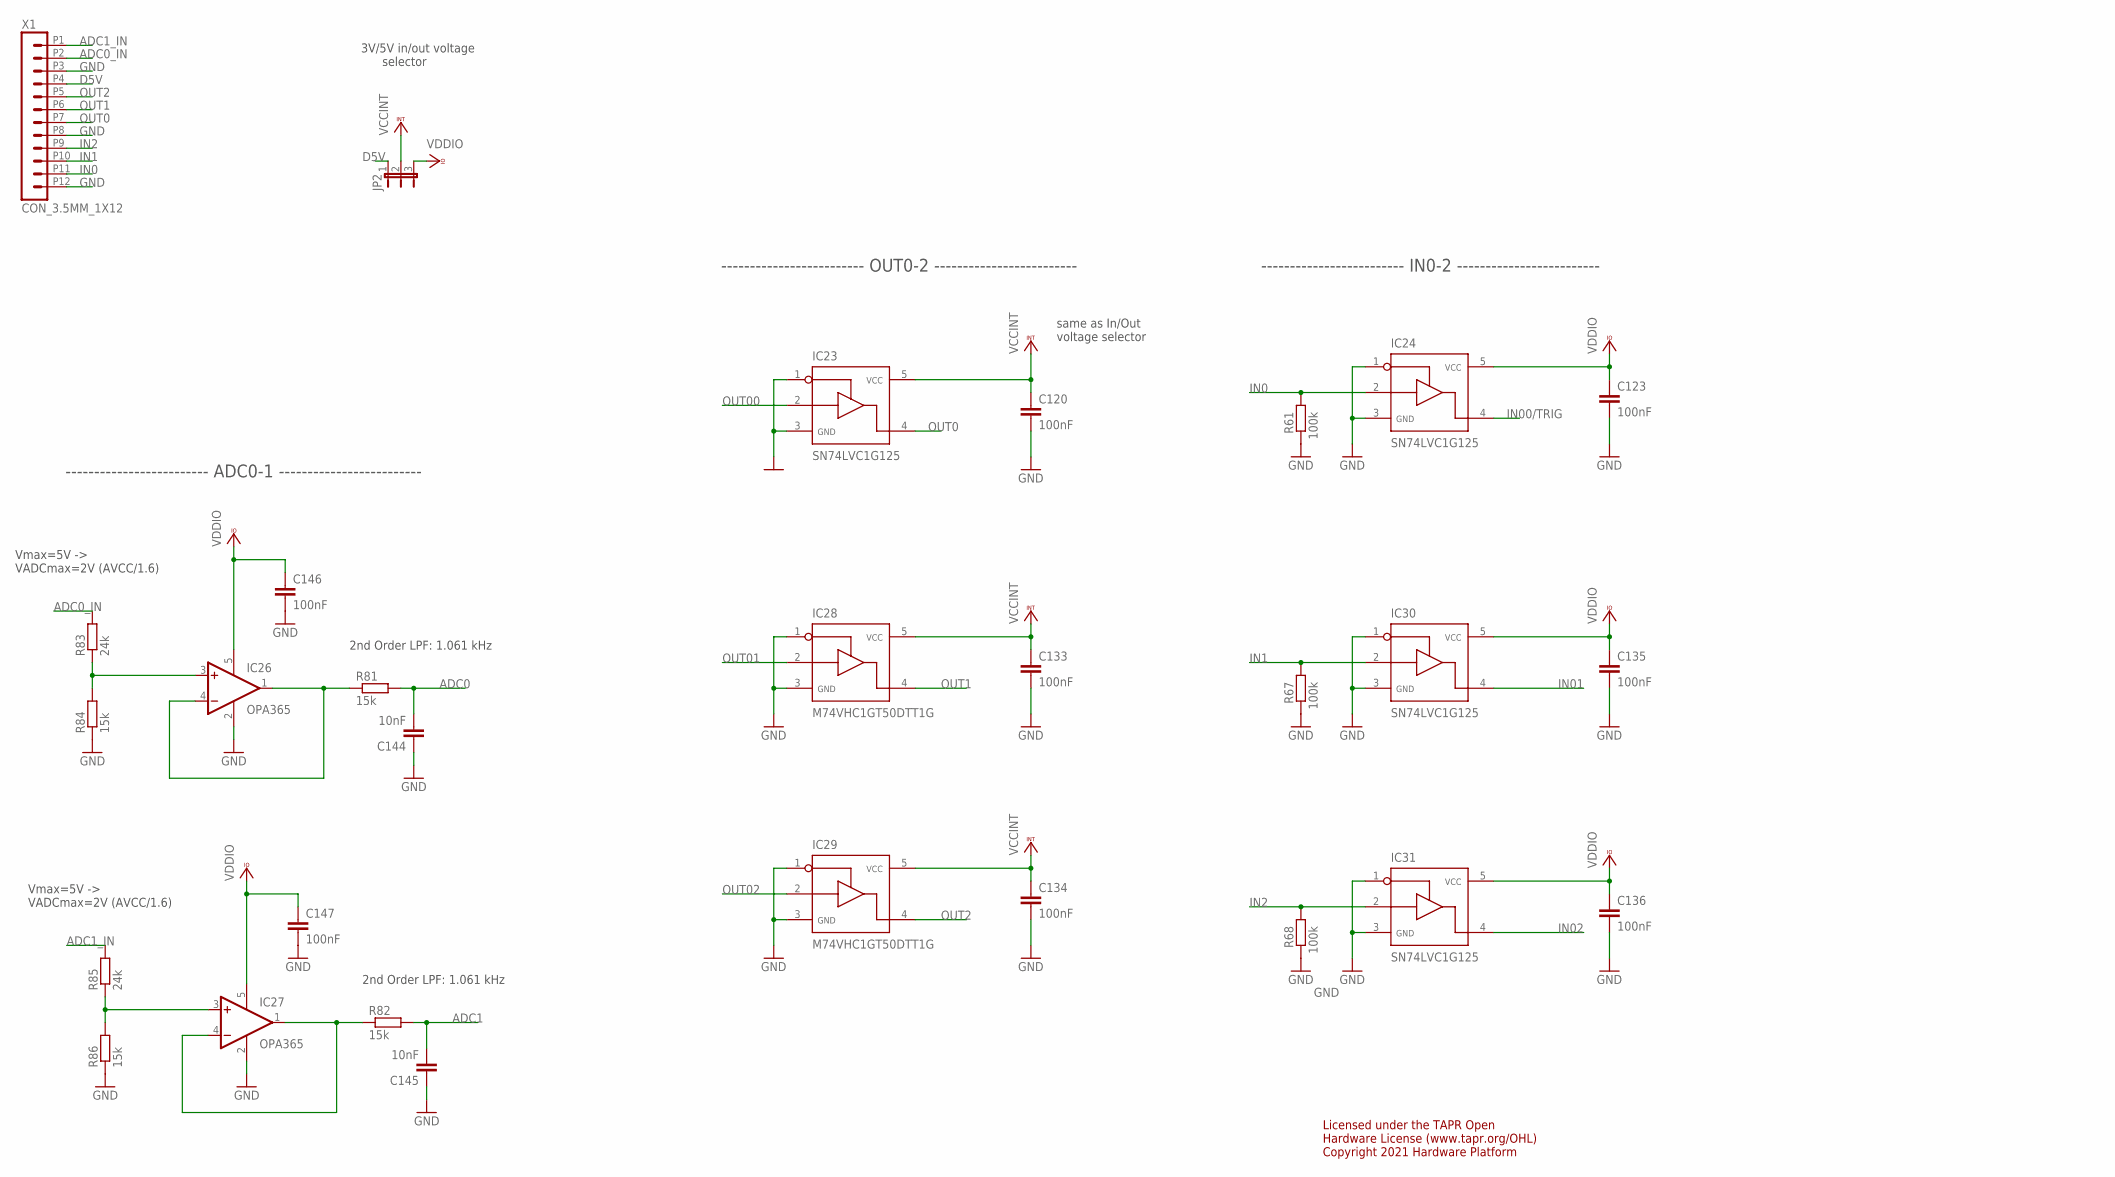
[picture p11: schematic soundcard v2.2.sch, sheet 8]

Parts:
C120, C123, C133, C134, C135, C136, C146, C147: 100nF; C0402
C144, C145: 10nF; C0402
IC23, IC24, IC30, IC31: SN74LVC1G125; SOT23-5
IC26, IC27: OPA365; SOT23-5
IC28, IC29: M74VHC1GT50DTT1G; SOT23-5
JP2: JP2E; JP2
R61, R67, R68: 100k; R0402
R81, R82, R84, R86: 15k; R0402
R83, R85: 24k; R0402
X1: CON_3.5MM_1X12

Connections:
ADC0: C144.2, R81.2; also elsewhere on the board
ADC0_IN: R83.2, X1.P2 (2)
ADC1: C145.2, R82.2; also elsewhere on the board
ADC1_IN: R85.2, X1.P1 (1)
D5V: JP2.1, X1.P4 (4); also elsewhere on the board
GND: C120.2, C123.2, C133.2, C134.2, C135.2, C136.2, C144.1, C145.1, C146.2, C147.2, IC23.1, IC23.3, IC24.1, IC24.3, IC26.2 (V-), IC27.2 (V-), IC28.1, IC28.3, IC29.1, IC29.3, IC30.1, IC30.3, IC31.1, IC31.3, R61.2, R67.2, R68.2, R84.1, R86.1, X1.P3 (3), X1.P8 (8), X1.P12 (12); also elsewhere on the board
IN0: IC24.2, R61.1, X1.P11 (11)
IN00/TRIG: IC24.4; also elsewhere on the board
IN1: IC30.2, R67.1, X1.P10 (10)
IN01: IC30.4; also elsewhere on the board
IN02: IC31.4; also elsewhere on the board
IN2: IC31.2, R68.1, X1.P9 (9)
unnamed: IC26.1 (OUT), IC26.4 (-IN), R81.1
unnamed: IC27.1 (OUT), IC27.4 (-IN), R82.1
unnamed: IC26.3 (+IN), R83.1, R84.2
unnamed: IC27.3 (+IN), R85.1, R86.2
OUT00: IC23.2; also elsewhere on the board
OUT0: IC23.4, X1.P7 (7)
OUT01: IC28.2; also elsewhere on the board
OUT1: IC28.4, X1.P6 (6)
OUT02: IC29.2; also elsewhere on the board
OUT2: IC29.4, X1.P5 (5)
VCCINT: C120.1, C133.1, C134.1, IC23.5, IC28.5, IC29.5, JP2.2
VCCIO: C123.1, C135.1, C136.1, C146.1, C147.1, IC24.5, IC26.5 (V+), IC27.5 (V+), IC30.5, IC31.5, JP2.3; also elsewhere on the board

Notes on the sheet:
3V/5V in/out voltage selector
same as In/Out voltage selector
Licensed under the TAPR Open Hardware License (www.tapr.org/OHL) Copyright 2021 Hardware Platform
2nd Order LPF: 1.061 kHz
Vmax=5V -> VADCmax=2V (AVCC/1.6)
------------------------- ADC0-1 -------------------------
------------------------- OUT0-2 -------------------------
------------------------- IN0-2 -------------------------

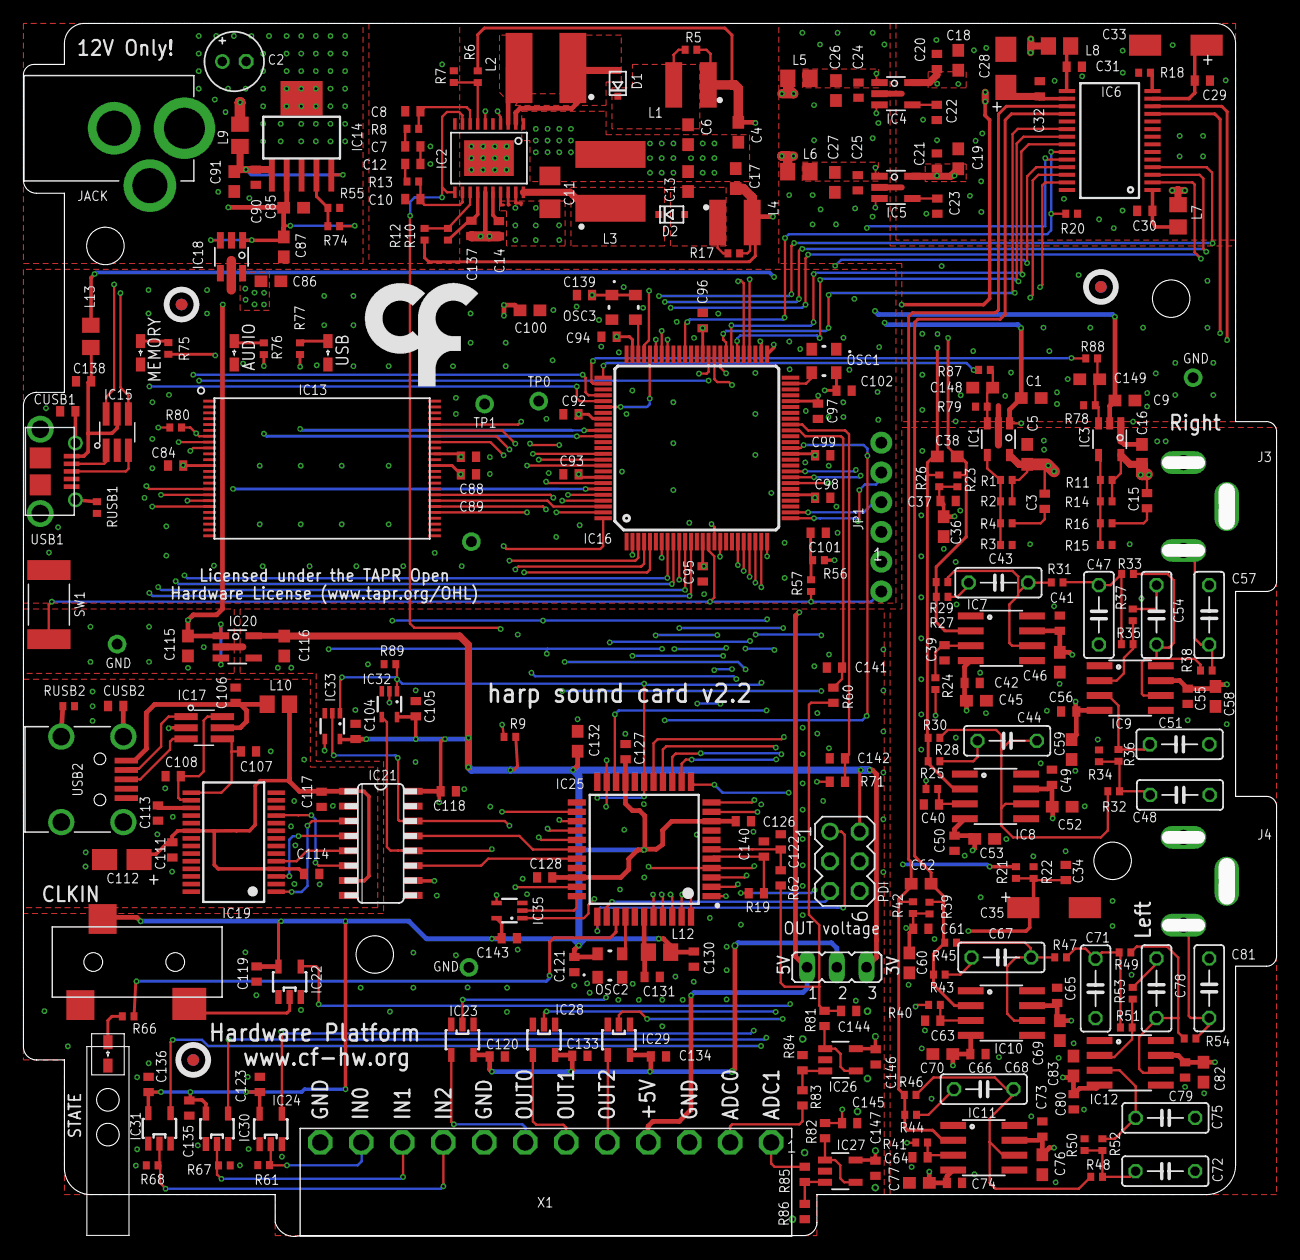
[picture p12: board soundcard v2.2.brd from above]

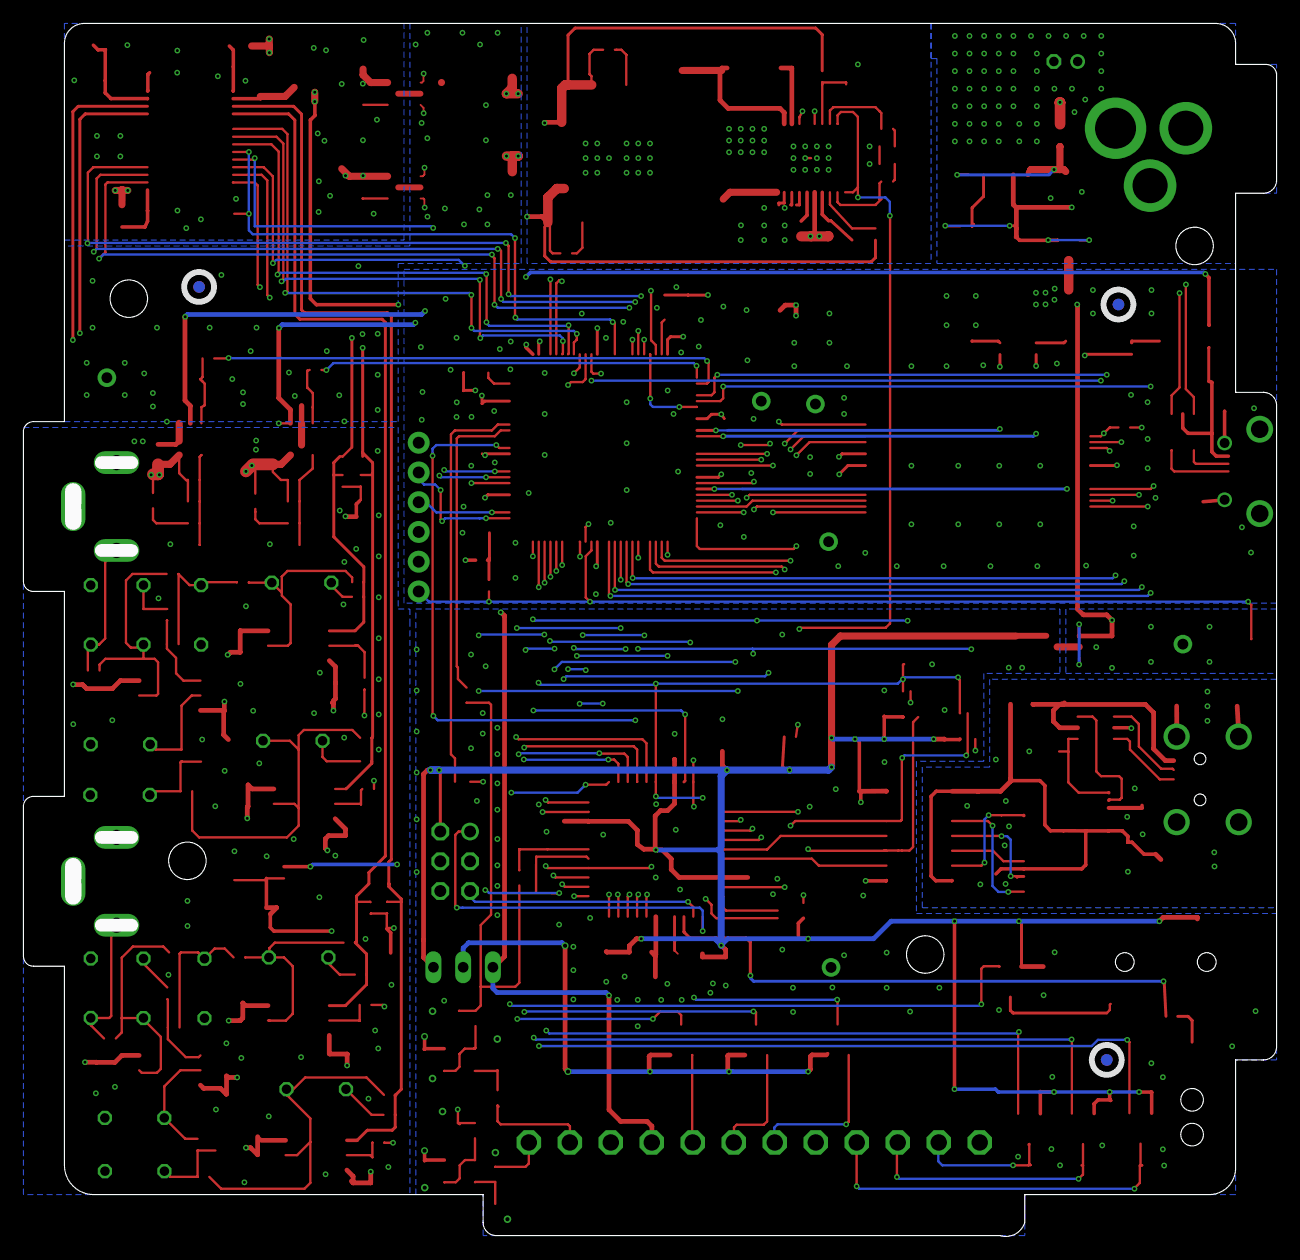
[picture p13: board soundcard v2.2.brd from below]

Board: 4 copper layers, 107.0 x 103.6 mm, 307 parts (3 on the bottom side), 190 nets.

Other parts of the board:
U$1: LED_PIPE_7513D2-L
U$2: LOGO_6
U$6, U$8, U$10, U$11, U$12, U$13: FIDUCIAL

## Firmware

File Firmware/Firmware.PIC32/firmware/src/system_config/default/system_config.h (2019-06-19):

/*******************************************************************************
  MPLAB Harmony System Configuration Header

  File Name:
    system_config.h

  Summary:
    Build-time configuration header for the system defined by this MPLAB Harmony
    project.

  Description:
    An MPLAB Project may have multiple configurations.  This file defines the
    build-time options for a single configuration.

  Remarks:
    This configuration header must not define any prototypes or data
    definitions (or include any files that do).  It only provides macro
    definitions for build-time configuration options that are not instantiated
    until used by another MPLAB Harmony module or application.

    Created with MPLAB Harmony Version 2.04
*******************************************************************************/

// DOM-IGNORE-BEGIN
/*******************************************************************************
Copyright (c) 2013-2015 released Microchip Technology Inc.  All rights reserved.

Microchip licenses to you the right to use, modify, copy and distribute
Software only when embedded on a Microchip microcontroller or digital signal
controller that is integrated into your product or third party product
(pursuant to the sublicense terms in the accompanying license agreement).

You should refer to the license agreement accompanying this Software for
additional information regarding your rights and obligations.

SOFTWARE AND DOCUMENTATION ARE PROVIDED AS IS WITHOUT WARRANTY OF ANY KIND,
EITHER EXPRESS OR IMPLIED, INCLUDING WITHOUT LIMITATION, ANY WARRANTY OF
MERCHANTABILITY, TITLE, NON-INFRINGEMENT AND FITNESS FOR A PARTICULAR PURPOSE.
IN NO EVENT SHALL MICROCHIP OR ITS LICENSORS BE LIABLE OR OBLIGATED UNDER
CONTRACT, NEGLIGENCE, STRICT LIABILITY, CONTRIBUTION, BREACH OF WARRANTY, OR
OTHER LEGAL EQUITABLE THEORY ANY DIRECT OR INDIRECT DAMAGES OR EXPENSES
INCLUDING BUT NOT LIMITED TO ANY INCIDENTAL, SPECIAL, INDIRECT, PUNITIVE OR
CONSEQUENTIAL DAMAGES, LOST PROFITS OR LOST DATA, COST OF PROCUREMENT OF
SUBSTITUTE GOODS, TECHNOLOGY, SERVICES, OR ANY CLAIMS BY THIRD PARTIES
(INCLUDING BUT NOT LIMITED TO ANY DEFENSE THEREOF), OR OTHER SIMILAR COSTS.
*******************************************************************************/
// DOM-IGNORE-END

#ifndef _SYSTEM_CONFIG_H
#define _SYSTEM_CONFIG_H

// *****************************************************************************
// *****************************************************************************
// Section: Included Files
// *****************************************************************************
// *****************************************************************************
/*  This section Includes other configuration headers necessary to completely
    define this configuration.
*/


// DOM-IGNORE-BEGIN
#ifdef __cplusplus  // Provide C++ Compatibility

extern "C" {

#endif
// DOM-IGNORE-END

// *****************************************************************************
// *****************************************************************************
// Section: System Service Configuration
// *****************************************************************************
// *****************************************************************************
// *****************************************************************************
/* Common System Service Configuration Options
*/
#define SYS_VERSION_STR           "2.04"
#define SYS_VERSION               20400

// *****************************************************************************
/* Clock System Service Configuration Options
*/
#define SYS_CLK_FREQ                        200000000ul
#define SYS_CLK_BUS_PERIPHERAL_1            100000000ul
#define SYS_CLK_BUS_PERIPHERAL_2            100000000ul
#define SYS_CLK_BUS_PERIPHERAL_3            3076923ul
#define SYS_CLK_BUS_PERIPHERAL_4            100000000ul
#define SYS_CLK_BUS_PERIPHERAL_5            100000000ul
#define SYS_CLK_BUS_PERIPHERAL_7            200000000ul
#define SYS_CLK_BUS_PERIPHERAL_8            100000000ul
#define SYS_CLK_BUS_REFERENCE_1             12288000ul
#define SYS_CLK_CONFIG_PRIMARY_XTAL         24000000ul
#define SYS_CLK_CONFIG_SECONDARY_XTAL       32768ul
   
/*** Ports System Service Configuration ***/
#define SYS_PORT_A_ANSEL        0x3F23
#define SYS_PORT_A_TRIS         0xFFFF
#define SYS_PORT_A_LAT          0x0000
#define SYS_PORT_A_ODC          0x0000
#define SYS_PORT_A_CNPU         0x001C
#define SYS_PORT_A_CNPD         0x0000
#define SYS_PORT_A_CNEN         0x0000

#define SYS_PORT_B_ANSEL        0x3FFE
#define SYS_PORT_B_TRIS         0x3FFE
#define SYS_PORT_B_LAT          0x0000
#define SYS_PORT_B_ODC          0x0000
#define SYS_PORT_B_CNPU         0x0000
#define SYS_PORT_B_CNPD         0x0000
#define SYS_PORT_B_CNEN         0x0000

#define SYS_PORT_C_ANSEL        0x9FFF
#define SYS_PORT_C_TRIS         0xFFFF
#define SYS_PORT_C_LAT          0x0000
#define SYS_PORT_C_ODC          0x0000
#define SYS_PORT_C_CNPU         0x0000
#define SYS_PORT_C_CNPD         0x0000
#define SYS_PORT_C_CNEN         0x0000

#define SYS_PORT_D_ANSEL        0xC1C0
#define SYS_PORT_D_TRIS         0xFFFF
#define SYS_PORT_D_LAT          0x0000
#define SYS_PORT_D_ODC          0x0000
#define SYS_PORT_D_CNPU         0x0000
#define SYS_PORT_D_CNPD         0x0000
#define SYS_PORT_D_CNEN         0x0000

#define SYS_PORT_E_ANSEL        0xFFF0
#define SYS_PORT_E_TRIS         0xFFFF
#define SYS_PORT_E_LAT          0x0000
#define SYS_PORT_E_ODC          0x0000
#define SYS_PORT_E_CNPU         0x0000
#define SYS_PORT_E_CNPD         0x0000
#define SYS_PORT_E_CNEN         0x0000

#define SYS_PORT_F_ANSEL        0xFEC0
#define SYS_PORT_F_TRIS         0xFFFF
#define SYS_PORT_F_LAT          0x0000
#define SYS_PORT_F_ODC          0x0000
#define SYS_PORT_F_CNPU         0x0000
#define SYS_PORT_F_CNPD         0x0000
#define SYS_PORT_F_CNEN         0x0000

#define SYS_PORT_G_ANSEL        0x8FFC
#define SYS_PORT_G_TRIS         0xFFFF
#define SYS_PORT_G_LAT          0x0000
#define SYS_PORT_G_ODC          0x0000
#define SYS_PORT_G_CNPU         0x0000
#define SYS_PORT_G_CNPD         0x0000
#define SYS_PORT_G_CNEN         0x0000


/*** Interrupt System Service Configuration ***/
#define SYS_INT                     true
/*** Timer System Service Configuration ***/
#define SYS_TMR_POWER_STATE             SYS_MODULE_POWER_RUN_FULL
#define SYS_TMR_DRIVER_INDEX            DRV_TMR_INDEX_0
#define SYS_TMR_MAX_CLIENT_OBJECTS      5
#define SYS_TMR_FREQUENCY               1000
#define SYS_TMR_FREQUENCY_TOLERANCE     10
#define SYS_TMR_UNIT_RESOLUTION         10000
#define SYS_TMR_CLIENT_TOLERANCE        10
#define SYS_TMR_INTERRUPT_NOTIFICATION  false

// *****************************************************************************
// *****************************************************************************
// Section: Driver Configuration
// *****************************************************************************
// *****************************************************************************

/*** I2S Driver Configuration ***/


#define DRV_I2S_INTERRUPT_MODE					true
#define DRV_I2S_CLIENTS_NUMBER					1
#define DRV_I2S_INSTANCES_NUMBER				1
#define DRV_I2S_STOP_IN_IDLE					false
#define DRV_I2S_PERIPHERAL_ID_IDX0				SPI_ID_4
#define DRV_I2S_USAGE_MODE_IDX0					DRV_I2S_MODE_MASTER
#define DRV_I2S_STOP_IN_IDLE_IDX0				false
#define SPI_BAUD_RATE_CLK_IDX0					SPI_BAUD_RATE_MCLK_CLOCK
#define DRV_I2S_BAUD_RATE                       96000
#define DRV_I2S_CLK_MODE_IDX0					DRV_I2S_CLOCK_MODE_IDLE_HIGH_EDGE_FALL
#define SPI_AUDIO_COMM_WIDTH_IDX0				SPI_AUDIO_COMMUNICATION_32DATA_32FIFO_32CHANNEL
#define SPI_AUDIO_TRANSMIT_MODE_IDX0			SPI_AUDIO_TRANSMIT_STEREO
#define SPI_INPUT_SAMPLING_PHASE_IDX0			SPI_INPUT_SAMPLING_PHASE_IN_MIDDLE
#define DRV_I2S_AUDIO_PROTOCOL_MODE_IDX0		DRV_I2S_AUDIO_I2S
#define DRV_I2S_TX_INT_SRC_IDX0					INT_SOURCE_SPI_4_TRANSMIT
#define DRV_I2S_RX_INT_SRC_IDX0					INT_SOURCE_SPI_4_RECEIVE
#define QUEUE_SIZE_TX_IDX0                      3
#define QUEUE_SIZE_RX_IDX0                      2
#define DRV_I2S_TX_DMA_CHANNEL_IDX0				DMA_CHANNEL_0
#define DRV_I2S_TX_DMA_SOURCE_IDX0				INT_SOURCE_DMA_0
#define DRV_I2S_POWER_STATE_IDX0				SYS_MODULE_POWER_RUN_FULL
#define DRV_I2S_QUEUE_DEPTH_COMBINED     		5

/*** Timer Driver Configuration ***/
#define DRV_TMR_INTERRUPT_MODE             true
#define DRV_TMR_INSTANCES_NUMBER           1
#define DRV_TMR_CLIENTS_NUMBER             1

/*** Timer Driver 0 Configuration ***/
#define DRV_TMR_PERIPHERAL_ID_IDX0          TMR_ID_1
#define DRV_TMR_INTERRUPT_SOURCE_IDX0       INT_SOURCE_TIMER_1
#define DRV_TMR_INTERRUPT_VECTOR_IDX0       INT_VECTOR_T1
#define DRV_TMR_ISR_VECTOR_IDX0             _TIMER_1_VECTOR
#define DRV_TMR_INTERRUPT_PRIORITY_IDX0     INT_PRIORITY_LEVEL1
#define DRV_TMR_INTERRUPT_SUB_PRIORITY_IDX0 INT_SUBPRIORITY_LEVEL0
#define DRV_TMR_CLOCK_SOURCE_IDX0           DRV_TMR_CLKSOURCE_INTERNAL
#define DRV_TMR_PRESCALE_IDX0               TMR_PRESCALE_VALUE_256
#define DRV_TMR_OPERATION_MODE_IDX0         DRV_TMR_OPERATION_MODE_16_BIT
#define DRV_TMR_ASYNC_WRITE_ENABLE_IDX0     false
#define DRV_TMR_POWER_STATE_IDX0            SYS_MODULE_POWER_RUN_FULL

 
// *****************************************************************************
// *****************************************************************************
// Section: Middleware & Other Library Configuration
// *****************************************************************************
// *****************************************************************************

/*** USB Driver Configuration ***/


/* Enables Device Support */
#define DRV_USBHS_DEVICE_SUPPORT      true

/* Disable Host Support */
#define DRV_USBHS_HOST_SUPPORT      false

/* Maximum USB driver instances */
#define DRV_USBHS_INSTANCES_NUMBER    1

/* Interrupt mode Disabled */
#define DRV_USBHS_INTERRUPT_MODE      false


/* Number of Endpoints used */
#define DRV_USBHS_ENDPOINTS_NUMBER    2




/*** USB Device Stack Configuration ***/










/* The USB Device Layer will not initialize the USB Driver */
#define USB_DEVICE_DRIVER_INITIALIZE_EXPLICIT

/* Maximum device layer instances */
#define USB_DEVICE_INSTANCES_NUMBER     1

/* EP0 size in bytes */
#define USB_DEVICE_EP0_BUFFER_SIZE      64








/* Endpoint Transfer Queue Size combined for Read and write */
#define USB_DEVICE_ENDPOINT_QUEUE_DEPTH_COMBINED    2


    
    
#define APP_READ_BUFFER_SIZE 65536  // Previously it was 512

/* Fulfill USB DMA transfer criteria */
#define APP_MAKE_BUFFER_DMA_READY  __attribute__((coherent)) __attribute__((aligned(16)))


/* Number of Endpoints used */    
#define APP_EP_BULK_IN  1

/* Number of Endpoints used */    
#define APP_EP_BULK_OUT 1


// *****************************************************************************
// *****************************************************************************
// Section: Application Configuration
// *****************************************************************************
// *****************************************************************************
/*** Application Defined Pins ***/


/*** Application Instance 0 Configuration ***/

//DOM-IGNORE-BEGIN
#ifdef __cplusplus
}
#endif
//DOM-IGNORE-END

#endif // _SYSTEM_CONFIG_H
/*******************************************************************************
 End of File
*/

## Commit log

2018-10-15 Added the firmware code for the sound card's controller (8 bits processor).
    [registers.xls]
2018-10-15 Added PCB and case files.
    [35RASMT2BHNTRX.SLDPRT, 7513D2-L.SLDPRT, CVM_BNC_Conector.SLDPRT, DC Barrel Power Jack_Connector.SLDPRT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]
2018-10-22 Added ability to save a description file up to 512 bytes in the device's memory.
2018-10-22 Updated assembly information.
2018-11-22 Corrected error that was crashing DMA when the number of samples was equal to 2048 x N + 2. Minor cleanup.
2018-12-14 Added and renamed registers. Some clean up.
    [registers.xls]
2019-02-20 Added ability to receive new sound data while playing a sound.
    [Memory Alocation.xlsx, Pinout list.xlsx]
2019-02-28 Updated bootloader to our case and added the dependencies' package to remove all local dependencies.
2019-02-28 Protected device when user sends new data and a sound is being produced with 192Ksample/sec.
2019-03-07 Corrected the bug that did not allow to produce correct sound in the first 512 samples.
2019-03-14 Updated some pin names.
    [Pinout list.xlsx]
2019-03-19 implemented command to clean a sound index or the entire memory.
    [registers.xls]
2019-03-19 Replaced PCB files with the version 1.1.
    [soundcard v1.1.brd, soundcard v1.1.sch, soundcard v1.1_BOM.xlsx, soundcard_BOM.xlsx]
2019-03-25 Minor changes and added gerbers.
    [soundcard v1.1.GBL, soundcard v1.1.GBO, soundcard v1.1.GBS, soundcard v1.1.GTL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]
2019-03-25 Added centroids.
    [soundcard v1.1_centroid_inches.csv, soundcard v1.1_centroid_millimeters.csv]
2019-03-26 Added BOM for assembly houses.
    [soundcard v1.1_BOM_assembly_house.xlsx, soundcard v1.1_BOM_complete.xlsx]
2019-03-26 Removed BOM for assembly houses.
    [soundcard v1.1_BOM.xlsx, soundcard v1.1_BOM_assembly_house.xlsx, soundcard v1.1_BOM_complete.xlsx]
2019-03-26 Minor corrections.
    [soundcard v1.1_BOM.xlsx]
2019-07-17 Added filter to return error if the index to play is bellow 2.
2020-05-24 Added case fabrication details.
    [Soundboard Case v1.1.STEP, soundboard_case_v1.1_BOM.xlsx]
2020-05-24 Added panel production files.
    [SB v1.1 - panel.brd, SB v1.1 - panel.drl, SB v1.1 - panel.sch, SB v1.1 - panel.xlsx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]
2022-09-23 organize PCB folder and add SB v1.1 files
    [35RASMT2BHNTRX.SLDPRT, 7513D2-L.SLDPRT, CVM_BNC_Conector.SLDPRT, DC Barrel Power Jack_Connector.SLDPRT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]
2023-03-29 Add prototype device schema and interface
2023-08-10 Refactor repository structure
    [Memory Alocation.xlsx, Pinout list.xlsx, registers.xls, soundboard_case_v1.1_BOM.xlsx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]
2023-12-06 Implementation of sin generator on ATxmega
    [registers.xls]
2023-12-06 Update to core 1.13
    [registers.xls]
2024-02-14 Update PCB version
    [soundcard v2.2.brd, soundcard v2.2.sch, soundcard v2.2_BOM.xlsx]
2024-04-09 Update YML to comply with device meta-schema
2024-04-10 Add support for specifying which device to update
2024-04-10 Ensure only Int32 sample type is used
2024-05-02 Removed not used registers and updated registers' description.
    [registers.xls]
2024-05-03 Removed more not used registers and created ADCx_CONF.
    [registers.xls]
2024-05-03 Moved register REG_COMMANDS to position 82.
    This is needed to keep the firmware update working.
    [registers.xls]
2024-06-20 Changed registers to U16
    [registers.xls]
2024-06-20 Added pulse to digital outputs and implemented defaults.
    [registers.xls]
2024-11-09 Update package metadata to embed device metadata
2024-11-10 Add harp-tech as source of device schema

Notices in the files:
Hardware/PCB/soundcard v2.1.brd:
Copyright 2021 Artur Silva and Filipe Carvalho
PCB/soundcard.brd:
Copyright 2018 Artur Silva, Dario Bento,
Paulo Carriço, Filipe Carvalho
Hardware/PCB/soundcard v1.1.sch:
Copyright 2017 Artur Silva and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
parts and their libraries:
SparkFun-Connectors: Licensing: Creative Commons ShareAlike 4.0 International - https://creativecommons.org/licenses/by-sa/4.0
